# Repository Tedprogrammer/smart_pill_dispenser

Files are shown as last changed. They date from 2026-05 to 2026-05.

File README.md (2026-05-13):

# Smart Pill Dispenser
An ESP32 based smart medication reminder and pill dispensing assistant designed for elderly users.

The system uses:
- RTC timekeeping
- LCD display
- LEDs
- buzzer alarms
- push button interaction
Purpose: to remind elderly with dementia when medication should be taken.

## Features
- Real time medication reminders
- Visual LED indicators
- Audible buzzer alarm
- LCD medication display
- Button acknowledgement system
- Battery powered operation

## Hardware
- ESP32 Dev Module
- DS3231 RTC
- 16x2 I2C LCD
- LEDs
- Push buttons
- Passive buzzer
- 18650 battery
- TP4056 charger module

## Prototype
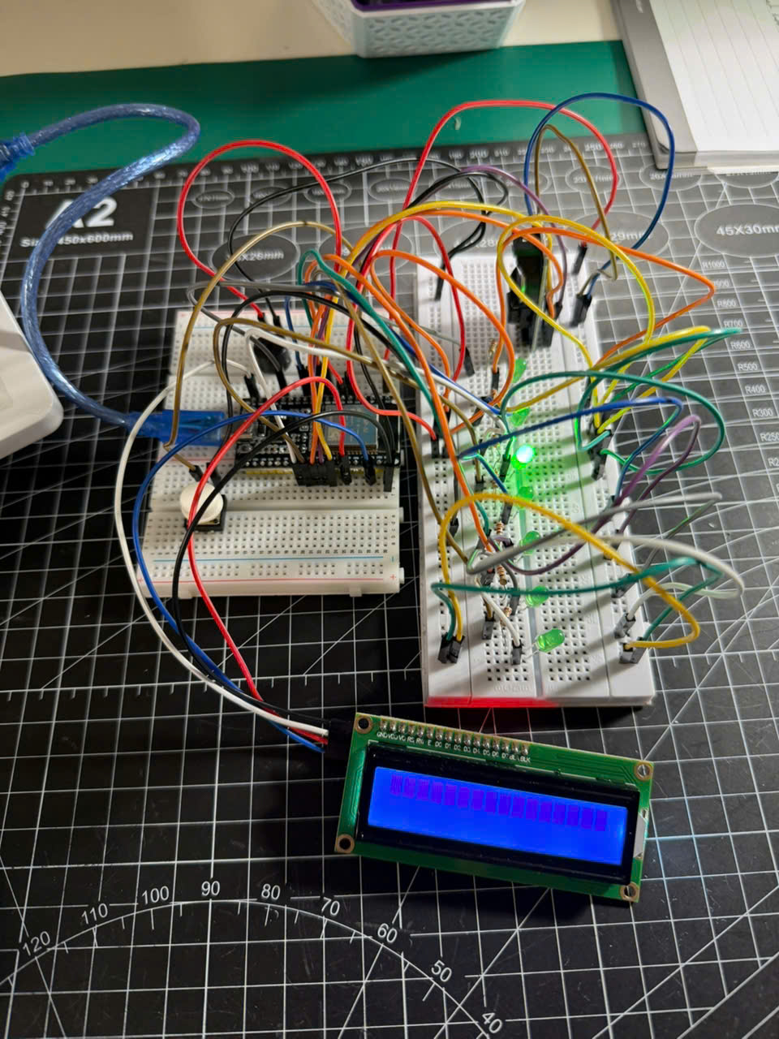
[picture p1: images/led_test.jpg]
LCD Test


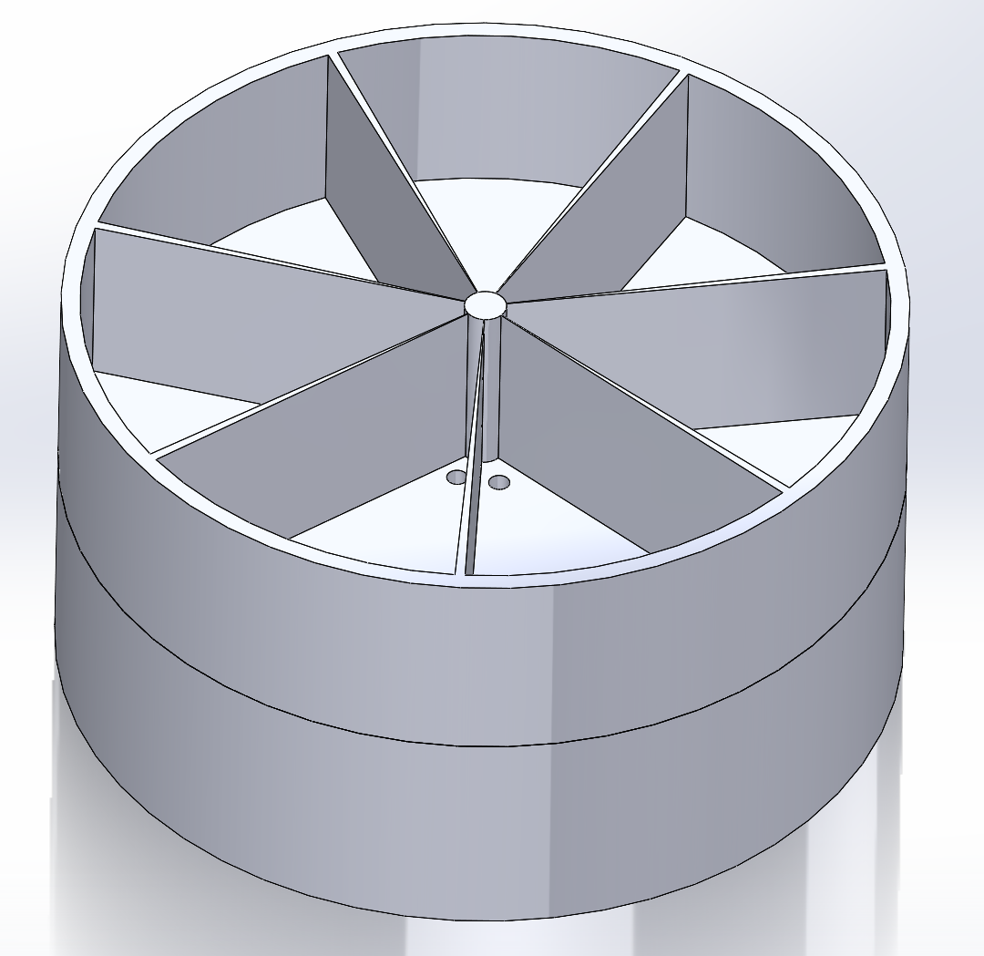
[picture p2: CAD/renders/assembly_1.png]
CAD Render


## Wiring Diagram

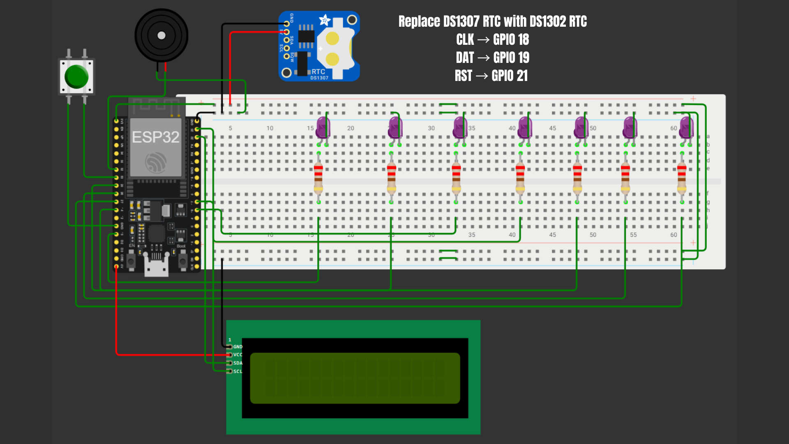
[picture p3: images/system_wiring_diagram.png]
System Wiring Diagram


The circuit was designed and simulated using Wokwi. The Wokwi project archive is available in the `simulation/` folder.

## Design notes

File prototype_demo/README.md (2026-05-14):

# Smart Pill Dispenser Prototype Demo

This prototype demonstrates the core functionality of the smart pill dispenser system designed for elderly users, especially dementia patients.

## Prototype Features

- 7 LED indicators representing weekly medication sections
- LCD display showing medication status
- Countdown system for next medication intake
- Buzzer alarm notification
- Push button acknowledgement system
- ESP32 based embedded control system

## Prototype Demonstration Logic

### Initial State

LCD displays:

Breakfast done
Lunch in 20 sec

The LEDs continuously blink in sequence every 3 seconds to simulate weekly medication compartments.

---

### Alarm State

After 20 seconds:

- LCD changes to:
  
  Time for lunch
  Press button

- Buzzer alarm activates periodically

---

### Confirmation State

When the push button is pressed:

- Alarm stops
- Medication is marked as taken
- LCD updates to:

  Lunch pill taken
  Next pill:1 hr

This demonstrates how the system helps dementia patients avoid double medication intake.

---

## Hardware Used

- ESP32 Dev Module
- DS1302 RTC Module
- I2C 16x2 LCD
- Active/Passive Buzzer
- Push Button
- 7 LEDs
- Breadboards and jumper wires

---

## Prototype Purpose

This prototype validates the user interaction flow and embedded control logic before full mechanical integration into the final cylindrical pill dispenser design.

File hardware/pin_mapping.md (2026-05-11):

# Pin Mapping

| Component | ESP32 Pin |
|---|---|
| LCD SDA | GPIO21 |
| LCD SCL | GPIO22 |
| DS1302 DAT | GPIO19 |
| DS1302 CLK | GPIO18 |
| DS1302 RST | GPIO5 |
| Monday LED | GPIO13 |
| Tuesday LED | GPIO14 |
| Wednesday LED | GPIO16 |
| Thursday LED | GPIO17 |
| Friday LED | GPIO25 |
| Saturday LED | GPIO26 |
| Sunday LED | GPIO27 |
| Buzzer | GPIO32 |
| Confirm Button | GPIO33 |

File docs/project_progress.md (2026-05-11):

# Project Progress

## Stage 1
Tested ESP32 over USB power.

## Stage 2
Tested individual LEDs.

## Stage 3
Tested passive buzzer.

## Stage 4
Tested push button input.

## Stage 5
Tested DS1302 real time clock module.

## Stage 6
Tested 16x2 I2C LCD display.

## Current Status
All core electronic components have been individually tested. The next stage is full system integration.

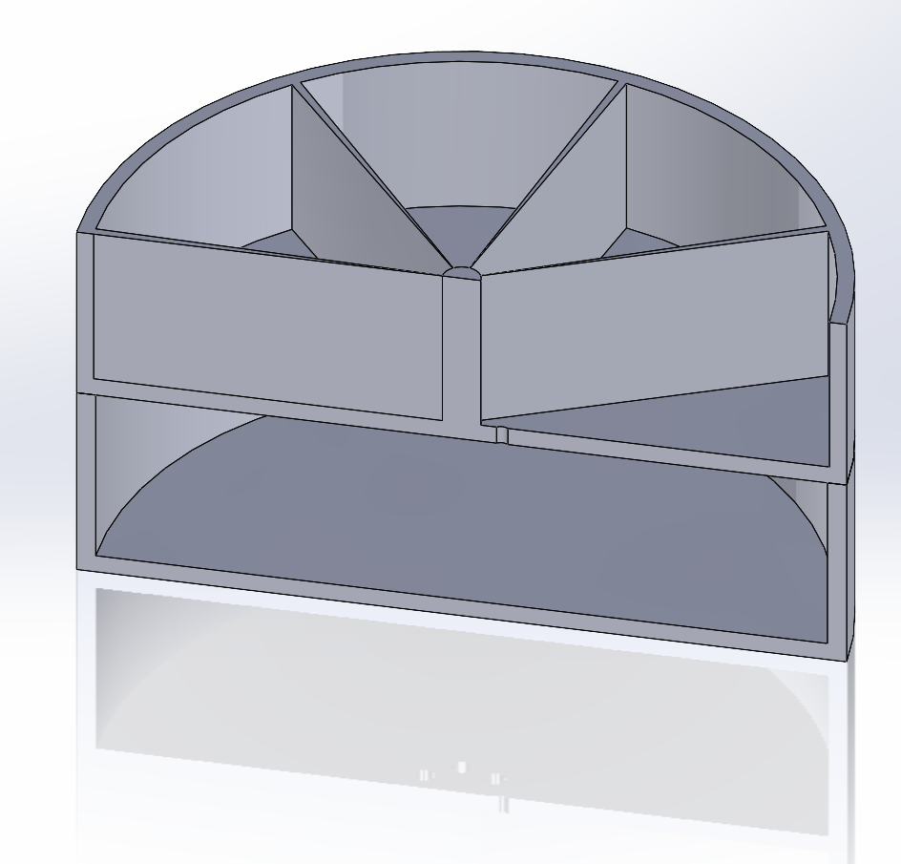
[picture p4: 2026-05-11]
CAD/renders/section_view.png

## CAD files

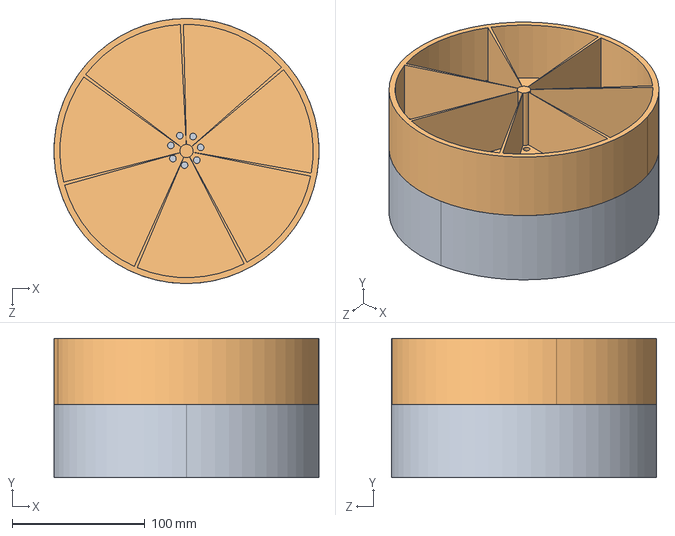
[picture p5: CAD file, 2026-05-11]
CAD/solidworks/assem_1.STEP
199.9 x 105.0 x 200.0 mm
base
top_2

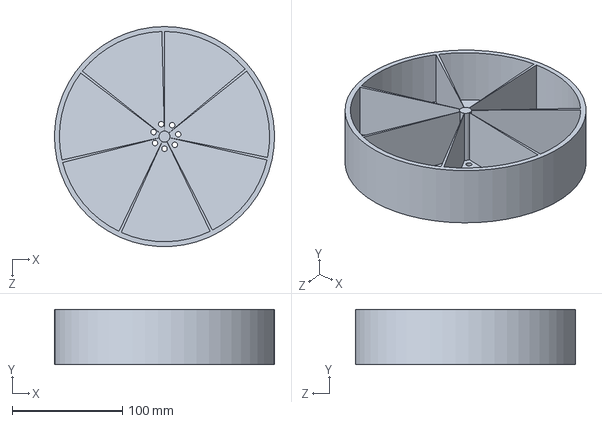
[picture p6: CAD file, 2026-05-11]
CAD/solidworks/lid.SLDPRT
199.9 x 50.0 x 199.8 mm

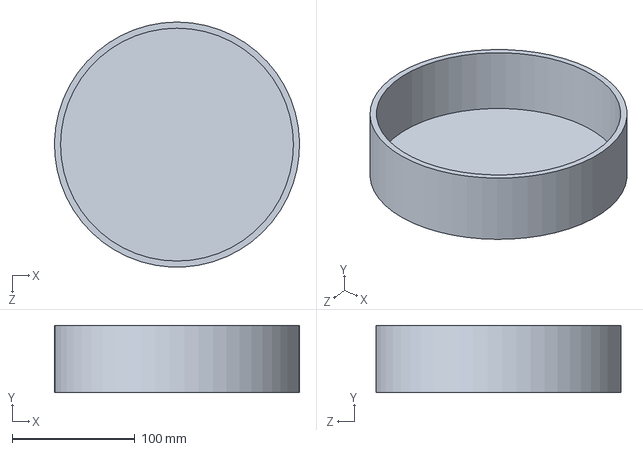
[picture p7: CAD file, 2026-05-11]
CAD/solidworks/base.SLDPRT
199.9 x 55.0 x 199.8 mm

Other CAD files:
CAD/solidworks/top_2.SLDPRT
CAD/solidworks/lid1.SLDPRT
CAD/solidworks/assem_1.SLDASM

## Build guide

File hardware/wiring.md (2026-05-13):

# Wiring Diagram

This file documents the electronic wiring for the smart pill dispenser prototype.

## Main Components

- ESP32 Dev Module
- RTC module
- 16x2 I2C LCD
- 7 LED indicators
- Passive buzzer
- Push button

## Wiring Diagram

System Wiring Diagram

## Notes

The wiring diagram was created using Wokwi and is used as the reference for the breadboard prototype.

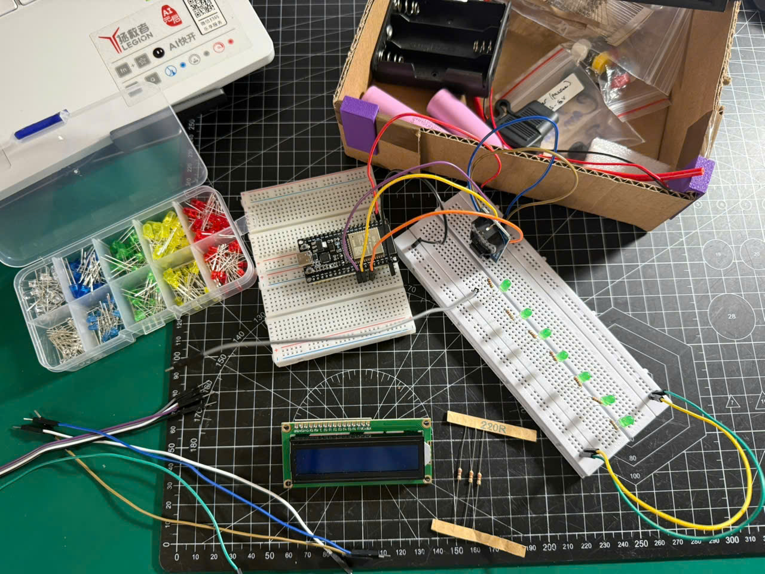
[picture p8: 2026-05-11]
images/breadboard_setup.jpg

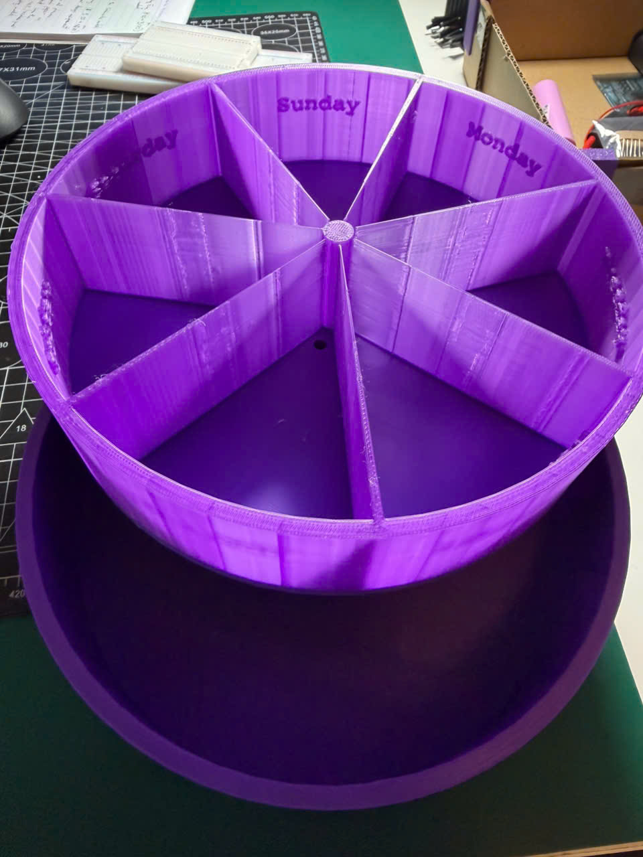
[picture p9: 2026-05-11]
images/3d_printed_v1.jpg

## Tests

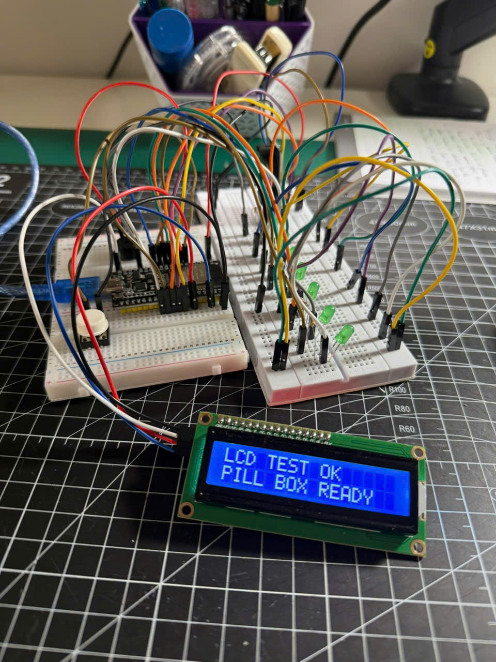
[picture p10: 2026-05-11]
images/lcd_test.jpg

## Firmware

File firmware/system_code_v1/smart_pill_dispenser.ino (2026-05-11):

#include <Wire.h>
#include <LiquidCrystal_I2C.h>
#include <ThreeWire.h>
#include <RtcDS1302.h>

// =========================
// LCD SETTINGS
// =========================

// LCD I2C address.
// Most modules use 0x27. Some use 0x3F.
LiquidCrystal_I2C lcd(0x27, 16, 2);

// ESP32 I2C pins for LCD.
const int LCD_SDA_PIN = 21;
const int LCD_SCL_PIN = 22;


// =========================
// RTC SETTINGS
// =========================

// DS1302 pins.
// Order required by library: DAT, CLK, RST
const int RTC_DAT_PIN = 19;
const int RTC_CLK_PIN = 18;
const int RTC_RST_PIN = 5;

ThreeWire rtcWire(RTC_DAT_PIN, RTC_CLK_PIN, RTC_RST_PIN);
RtcDS1302<ThreeWire> Rtc(rtcWire);


// =========================
// OUTPUT AND INPUT PINS
// =========================

// Seven LEDs represent seven days.
const int ledPins[7] = {
  13,  // Monday
  14,  // Tuesday
  16,  // Wednesday
  17,  // Thursday
  25,  // Friday
  26,  // Saturday
  27   // Sunday
};

// Short day names for LCD.
const char* dayNames[7] = {
  "MON", "TUE", "WED", "THU", "FRI", "SAT", "SUN"
};

// Passive buzzer pin.
const int buzzerPin = 32;

// Confirm button pin.
// Button should connect GPIO33 to GND when pressed.
const int buttonPin = 33;


// =========================
// MEDICATION SCHEDULE
// =========================

// Each Dose stores one medication time.
struct Dose {
  int hour;          // Dose hour in 24 hour format
  int minute;        // Dose minute
  int tablets;       // Number of tablets to display
  const char* label; // Text shown on LCD
};

// For testing, set one time close to current RTC time.
// Example: if current time is 14:35, set first dose to 14:36.
Dose doses[] = {
  {8, 0, 2, "Morning"},
  {13, 0, 1, "Noon"},
  {20, 0, 2, "Night"}
};

// Total number of dose times.
const int doseCount = sizeof(doses) / sizeof(doses[0]);


// =========================
// ALARM STATE VARIABLES
// =========================

// True when medication alarm is currently active.
bool alarmActive = false;

// Stores which dose is currently alarming.
int activeDoseIndex = -1;

// Stores which day LED should be active.
int activeDayIndex = -1;

// This records whether medication was taken.
// First index is day: 0 Monday to 6 Sunday.
// Second index is dose number.
bool medicationTaken[7][10];

// Used to reset medicationTaken when date changes.
int lastKnownDay = -1;
int lastKnownMonth = -1;
int lastKnownYear = -1;


// =========================
// TIMING VARIABLES
// =========================

// When alarm started.
unsigned long alarmStartMillis = 0;

// LED stays solid for this duration before buzzer starts.
const unsigned long LED_ONLY_TIME = 5000;

// Used for buzzer timing.
unsigned long lastBuzzerMillis = 0;

// Buzzer beeps once per second.
const unsigned long BUZZER_INTERVAL = 1000;

// Buzzer beep duration.
const unsigned long BUZZER_ON_TIME = 180;

// True while buzzer is currently on.
bool buzzerIsOn = false;

// Used to avoid refreshing LCD too fast.
unsigned long lastLcdUpdate = 0;


// =========================
// SETUP
// =========================

void setup() {
  Serial.begin(115200);

  // Start LCD I2C communication.
  Wire.begin(LCD_SDA_PIN, LCD_SCL_PIN);

  // Start LCD.
  lcd.init();
  lcd.backlight();

  // Start RTC.
  Rtc.Begin();

  // Start RTC if not running.
  if (!Rtc.GetIsRunning()) {
    Rtc.SetIsRunning(true);
  }

  // Configure LED pins.
  for (int i = 0; i < 7; i++) {
    pinMode(ledPins[i], OUTPUT);
    digitalWrite(ledPins[i], LOW);
  }

  // Configure buzzer.
  pinMode(buzzerPin, OUTPUT);
  noTone(buzzerPin);

  // Configure button with internal pullup.
  // Normal state is HIGH.
  // Pressed state is LOW.
  pinMode(buttonPin, INPUT_PULLUP);

  clearMedicationRecords();

  lcd.clear();
  lcd.setCursor(0, 0);
  lcd.print("Smart Pill Box");
  lcd.setCursor(0, 1);
  lcd.print("System Ready");

  delay(1500);
}


// =========================
// MAIN LOOP
// =========================

void loop() {
  RtcDateTime now = Rtc.GetDateTime();

  int todayIndex = convertRtcDayToIndex(now.DayOfWeek());

  resetRecordsIfNewDay(now);

  checkForDoseTime(now, todayIndex);

  checkButton();

  if (alarmActive) {
    runAlarm(now);
  } else {
    showNormalScreen(now, todayIndex);
  }
}


// =========================
// CHECK MEDICATION TIME
// =========================

void checkForDoseTime(RtcDateTime now, int todayIndex) {
  if (alarmActive) {
    return;
  }

  for (int i = 0; i < doseCount; i++) {
    bool timeMatches =
      now.Hour() == doses[i].hour &&
      now.Minute() == doses[i].minute;

    bool alreadyTaken =
      medicationTaken[todayIndex][i];

    if (timeMatches && !alreadyTaken) {
      startAlarm(todayIndex, i);
      return;
    }
  }
}


// =========================
// START ALARM
// =========================

void startAlarm(int dayIndex, int doseIndex) {
  alarmActive = true;
  activeDayIndex = dayIndex;
  activeDoseIndex = doseIndex;

  alarmStartMillis = millis();
  lastBuzzerMillis = 0;
  buzzerIsOn = false;

  allLedsOff();

  // First stage: LED turns on immediately.
  digitalWrite(ledPins[activeDayIndex], HIGH);

  Serial.println("Medication alarm started");
}


// =========================
// RUN ALARM
// =========================

void runAlarm(RtcDateTime now) {
  showAlarmScreen();

  unsigned long elapsed = millis() - alarmStartMillis;

  // First 5 seconds: LED only, no buzzer.
  if (elapsed < LED_ONLY_TIME) {
    digitalWrite(ledPins[activeDayIndex], HIGH);
    noTone(buzzerPin);
    return;
  }

  // After 5 seconds: LED remains on and buzzer beeps every second.
  digitalWrite(ledPins[activeDayIndex], HIGH);

  unsigned long currentMillis = millis();

  if (!buzzerIsOn && currentMillis - lastBuzzerMillis >= BUZZER_INTERVAL) {
    tone(buzzerPin, 2000);
    buzzerIsOn = true;
    lastBuzzerMillis = currentMillis;
  }

  if (buzzerIsOn && currentMillis - lastBuzzerMillis >= BUZZER_ON_TIME) {
    noTone(buzzerPin);
    buzzerIsOn = false;
  }
}


// =========================
// BUTTON HANDLING
// =========================

void checkButton() {
  if (digitalRead(buttonPin) == LOW) {
    delay(50);

    if (digitalRead(buttonPin) == LOW) {
      if (alarmActive) {
        confirmMedicationTaken();
      }

      while (digitalRead(buttonPin) == LOW) {
        delay(10);
      }
    }
  }
}


// =========================
// CONFIRM MEDICATION TAKEN
// =========================

void confirmMedicationTaken() {
  medicationTaken[activeDayIndex][activeDoseIndex] = true;

  alarmActive = false;

  allLedsOff();
  noTone(buzzerPin);

  Serial.print("Medication taken: ");
  Serial.print(dayNames[activeDayIndex]);
  Serial.print(" ");
  Serial.println(doses[activeDoseIndex].label);

  lcd.clear();
  lcd.setCursor(0, 0);
  lcd.print("Dose Confirmed");
  lcd.setCursor(0, 1);
  lcd.print("Marked Taken");

  delay(2000);

  activeDayIndex = -1;
  activeDoseIndex = -1;
}


// =========================
// LCD NORMAL SCREEN
// =========================

void showNormalScreen(RtcDateTime now, int todayIndex) {
  if (millis() - lastLcdUpdate < 1000) {
    return;
  }

  lastLcdUpdate = millis();

  lcd.clear();

  lcd.setCursor(0, 0);
  lcd.print(dayNames[todayIndex]);
  lcd.print(" ");

  printTwoDigitsToLcd(now.Hour());
  lcd.print(":");
  printTwoDigitsToLcd(now.Minute());
  lcd.print(":");
  printTwoDigitsToLcd(now.Second());

  lcd.setCursor(0, 1);
  lcd.print("Next ");
  lcd.print(doses[0].hour);
  lcd.print(":");
  printTwoDigitsToLcd(doses[0].minute);
  lcd.print(" ");
  lcd.print(doses[0].tablets);
  lcd.print(" tab");
}


// =========================
// LCD ALARM SCREEN
// =========================

void showAlarmScreen() {
  if (millis() - lastLcdUpdate < 500) {
    return;
  }

  lastLcdUpdate = millis();

  lcd.clear();

  lcd.setCursor(0, 0);
  lcd.print(dayNames[activeDayIndex]);
  lcd.print(" ");
  lcd.print(doses[activeDoseIndex].label);

  lcd.setCursor(0, 1);
  lcd.print("Take ");
  lcd.print(doses[activeDoseIndex].tablets);
  lcd.print(" tablet");
}


// =========================
// RESET DAILY RECORDS
// =========================

void resetRecordsIfNewDay(RtcDateTime now) {
  if (
    now.Day() != lastKnownDay ||
    now.Month() != lastKnownMonth ||
    now.Year() != lastKnownYear
  ) {
    clearMedicationRecords();

    lastKnownDay = now.Day();
    lastKnownMonth = now.Month();
    lastKnownYear = now.Year();

    Serial.println("New day detected. Medication records cleared.");
  }
}


// =========================
// HELPER FUNCTIONS
// =========================

void clearMedicationRecords() {
  for (int day = 0; day < 7; day++) {
    for (int dose = 0; dose < 10; dose++) {
      medicationTaken[day][dose] = false;
    }
  }
}

void allLedsOff() {
  for (int i = 0; i < 7; i++) {
    digitalWrite(ledPins[i], LOW);
  }
}

int convertRtcDayToIndex(uint8_t rtcDay) {
  // Makuna library normally uses:
  // Sunday = 0
  // Monday = 1
  // Tuesday = 2
  // ...
  // Saturday = 6

  if (rtcDay == 0) {
    return 6; // Sunday becomes index 6
  }

  return rtcDay - 1; // Monday becomes index 0
}

void printTwoDigitsToLcd(int number) {
  if (number < 10) {
    lcd.print("0");
  }

  lcd.print(number);
}

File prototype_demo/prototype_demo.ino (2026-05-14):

#include <Wire.h>
#include <LiquidCrystal_I2C.h>

LiquidCrystal_I2C lcd(0x27, 16, 2);

// LCD
const int LCD_SDA_PIN = 21;
const int LCD_SCL_PIN = 22;

// LEDs
const int ledPins[7] = {13, 14, 16, 17, 25, 26, 27};

// Buzzer and button
const int buzzerPin = 32;
const int buttonPin = 33;

// Demo timing
const unsigned long countdownSeconds = 20;
const unsigned long ledInterval = 3000;
const unsigned long buzzerInterval = 1000;
const unsigned long buzzerDuration = 250;

unsigned long countdownStartMillis = 0;
unsigned long lastLedMillis = 0;
unsigned long lastBuzzerMillis = 0;
unsigned long buzzerStartMillis = 0;

int currentLed = 0;

bool alarmActive = false;
bool medicationTaken = false;
bool buzzerOn = false;

void setup() {
  Serial.begin(115200);

  Wire.begin(LCD_SDA_PIN, LCD_SCL_PIN);

  lcd.init();
  lcd.backlight();
  lcd.clear();

  for (int i = 0; i < 7; i++) {
    pinMode(ledPins[i], OUTPUT);
    digitalWrite(ledPins[i], LOW);
  }

  pinMode(buzzerPin, OUTPUT);
  noTone(buzzerPin);

  pinMode(buttonPin, INPUT_PULLUP);

  countdownStartMillis = millis();

  lcd.setCursor(0, 0);
  lcd.print("Breakfast done");
  lcd.setCursor(0, 1);
  lcd.print("Lunch in 20 sec");
}

void loop() {
  runLedSequence();

  if (!alarmActive && !medicationTaken) {
    runCountdown();
  }

  if (alarmActive) {
    showAlarmScreen();
    runBuzzerAlarm();
    checkButton();
  }

  if (medicationTaken) {
    showTakenScreen();
  }
}

void runLedSequence() {
  if (millis() - lastLedMillis >= ledInterval) {
    lastLedMillis = millis();

    for (int i = 0; i < 7; i++) {
      digitalWrite(ledPins[i], LOW);
    }

    digitalWrite(ledPins[currentLed], HIGH);

    currentLed++;
    if (currentLed >= 7) {
      currentLed = 0;
    }
  }
}

void runCountdown() {
  unsigned long elapsed = (millis() - countdownStartMillis) / 1000;
  int remaining = countdownSeconds - elapsed;

  if (remaining > 0) {
    lcd.setCursor(0, 0);
    lcd.print("Breakfast done  ");

    lcd.setCursor(0, 1);
    lcd.print("Lunch in ");
    lcd.print(remaining);
    lcd.print(" sec   ");
  } else {
    alarmActive = true;
    lastBuzzerMillis = millis();
    Serial.println("Lunch alarm active");
  }
}

void showAlarmScreen() {
  lcd.setCursor(0, 0);
  lcd.print("Time for lunch ");

  lcd.setCursor(0, 1);
  lcd.print("Press button   ");
}

void runBuzzerAlarm() {
  unsigned long now = millis();

  if (!buzzerOn && now - lastBuzzerMillis >= buzzerInterval) {
    tone(buzzerPin, 2000);
    buzzerOn = true;
    buzzerStartMillis = now;
  }

  if (buzzerOn && now - buzzerStartMillis >= buzzerDuration) {
    noTone(buzzerPin);
    buzzerOn = false;
    lastBuzzerMillis = now;
  }
}

void checkButton() {
  if (digitalRead(buttonPin) == LOW) {
    delay(50);

    if (digitalRead(buttonPin) == LOW) {
      noTone(buzzerPin);
      buzzerOn = false;
      alarmActive = false;
      medicationTaken = true;

      lcd.clear();
      lcd.setCursor(0, 0);
      lcd.print("Lunch pill taken");
      lcd.setCursor(0, 1);
      lcd.print("Next pill:1 hr");

      Serial.println("Lunch pill marked as taken");

      while (digitalRead(buttonPin) == LOW) {
        delay(10);
      }
    }
  }
}

void showTakenScreen() {
  lcd.setCursor(0, 0);
  lcd.print("Lunch pill taken");

  lcd.setCursor(0, 1);
  lcd.print("Next pill: 1 hr");
}

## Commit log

2026-05-11 Add LED test script for controlling multiple LEDs
2026-05-11 Add ESP32 pin mapping
2026-05-11 Add hardware prototype images
2026-05-11 Add prototype section with images to README
2026-05-11 Include assembly render in README
    Added assembly render image to the README.
2026-05-11 Update assembly render image in README
2026-05-13 Add wiring documentation
2026-05-14 Add prototype demo for lunch reminder system
2026-05-14 Add README for Smart Pill Dispenser prototype
    Added detailed README for the Smart Pill Dispenser prototype, outlining features, demonstration logic, hardware used, and purpose.
